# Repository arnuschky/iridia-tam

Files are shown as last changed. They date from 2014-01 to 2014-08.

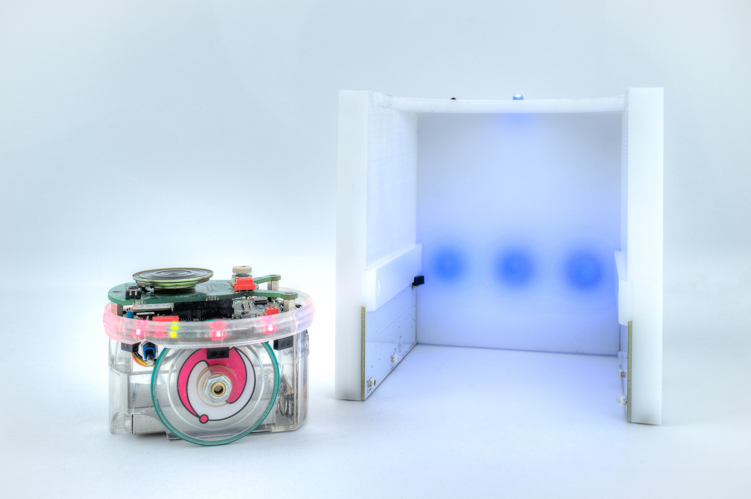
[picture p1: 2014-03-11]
photos/tam_v5_simple_epuck-surreal.jpg

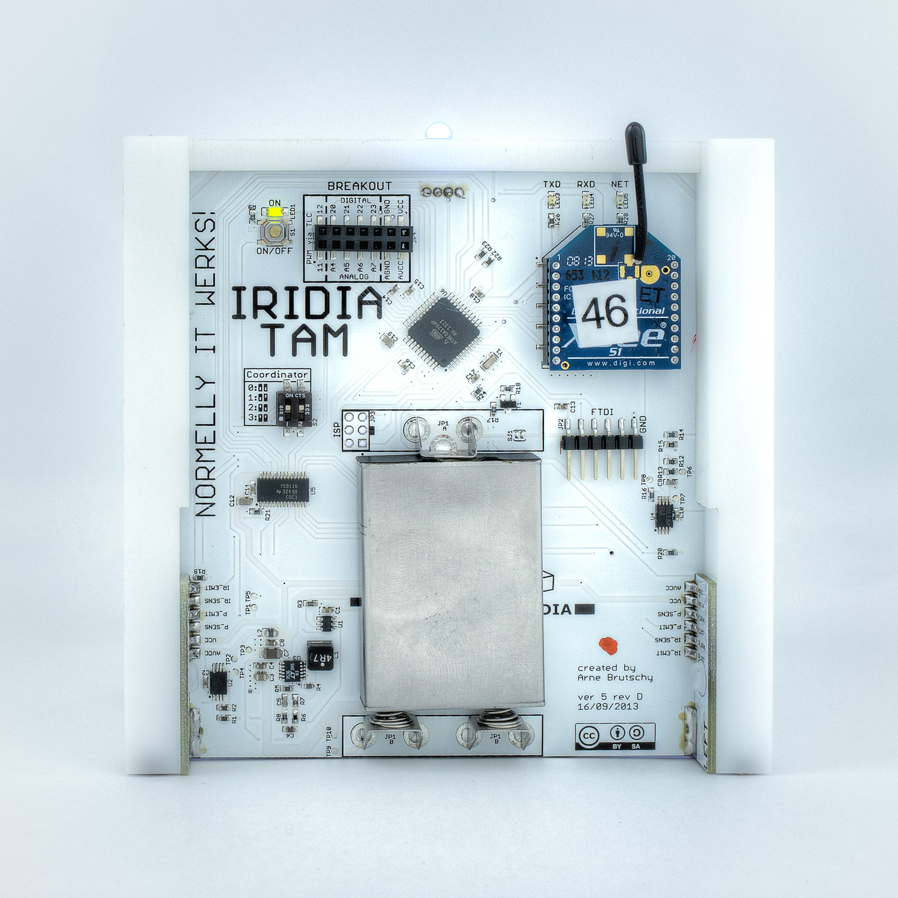
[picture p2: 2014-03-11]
photos/tam_v5_back-surreal.jpg

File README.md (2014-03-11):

IRIDIA-TAM
==========

The IRIDIA TAM (Task Abstraction Module), a device whose function is to represent tasks that have to be performed by e-puck robots in laboratory experiments.

 * Website: http://arnuschky.github.com/iridia-tam/  
 * GitHub: https://github.com/arnuschky/iridia-tam/  
 * Repository: http://arnuschky.github.com/iridia-tam/  
 
Current version of the TAM: version 5, revision D.

The GitHub repository contains all files required for producing and using the TAM. In detail, the different directories contain:

3dmodel
-------

A 3D model of the TAM, created by using the free version of Google Sketchup (version 8). Models of the PCBs have been created using EagleUp (http://eagleup.wordpress.com/).

Additionally, the directory contains 2D plans of the plastic shell in PDF format. These plans were used to produce the plastic shell (machined from POM plastic).

coordinator
----------

This directory contains the coordinator, the central software written in Java that controls all TAMs in a given experiment. The researcher can use the coordinator software to set the behavior of the TAMs, define their interrelationships and collect statistics. Due to the use of Java, the software it platform-independent.

The directory also includes a modified version of the Xbee-api, an open-source project to access Xbee modules using Java. See http://code.google.com/p/xbee-api/ for more information. The project has been adapted to use the Digimesh mesh networking prototcol. If desired, one could also use simple point-to-point communication or the more advanced Zigbee prototcol.

electronics
-----------

This directory contains the project files created using Eagle (non-free version, due to PCB size) and the Arduino libraries and firmware.

### electronics/eagle

Contains the CAD files (board and schematics) for CADSoft Eagle (Version 6). 
Additionally, a library with custom footprints is also included in the repository.

### electronics/arduino

Sourcecode of the TAM's firmware ("sketchbook" in Arduino-speech). There are also a number of libraries included on which the firmware depends. Some of these libraries have been written or modified by us:

 - ircom - library that allows to communicate between the TAM and the epuck using the proximity sensor of the epuck
 - TLC59116 - generic TLC59116 library, adapted from http://brmlab.cz/project/ledbar (CC Attribution-Noncommercial-Share Alike 3.0 Unported License)
 - Xbee - library for using Xbee modules with the Arduino by Andrew Rapp, adapted to work with Digimesh networks and software serial ports (GPL 3)

Others are 3rd party open-source projects included for convenience:

 - I2C - fast I2C library by Wayne Truchsess (LGPL) http://dsscircuits.com/articles/arduino-i2c-master-library.html

photos
------

High-res photos of the TAM version 5, revision D.

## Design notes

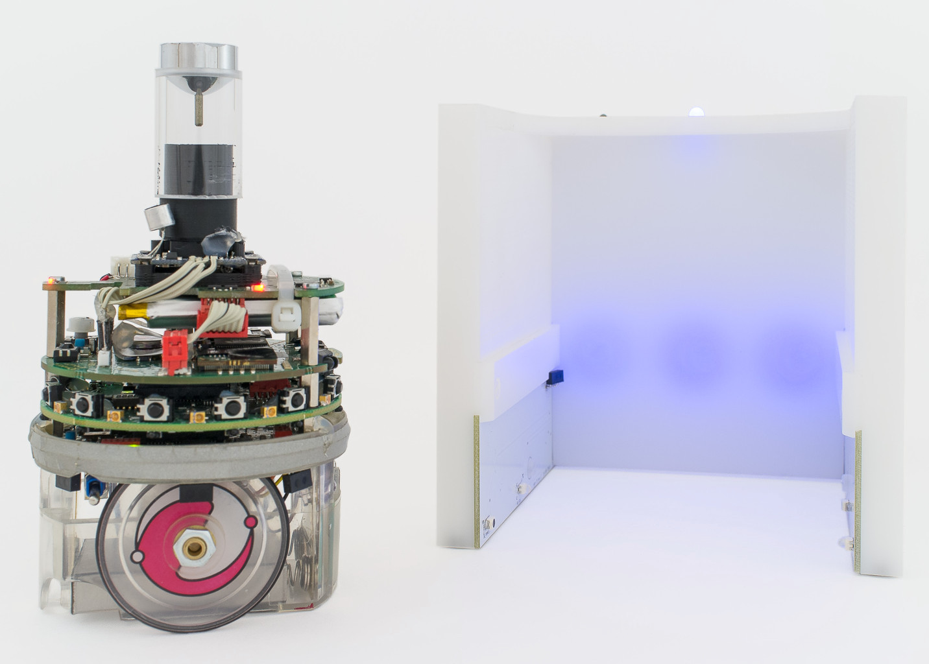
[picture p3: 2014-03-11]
photos/tam_v5_complex_epuck.jpg

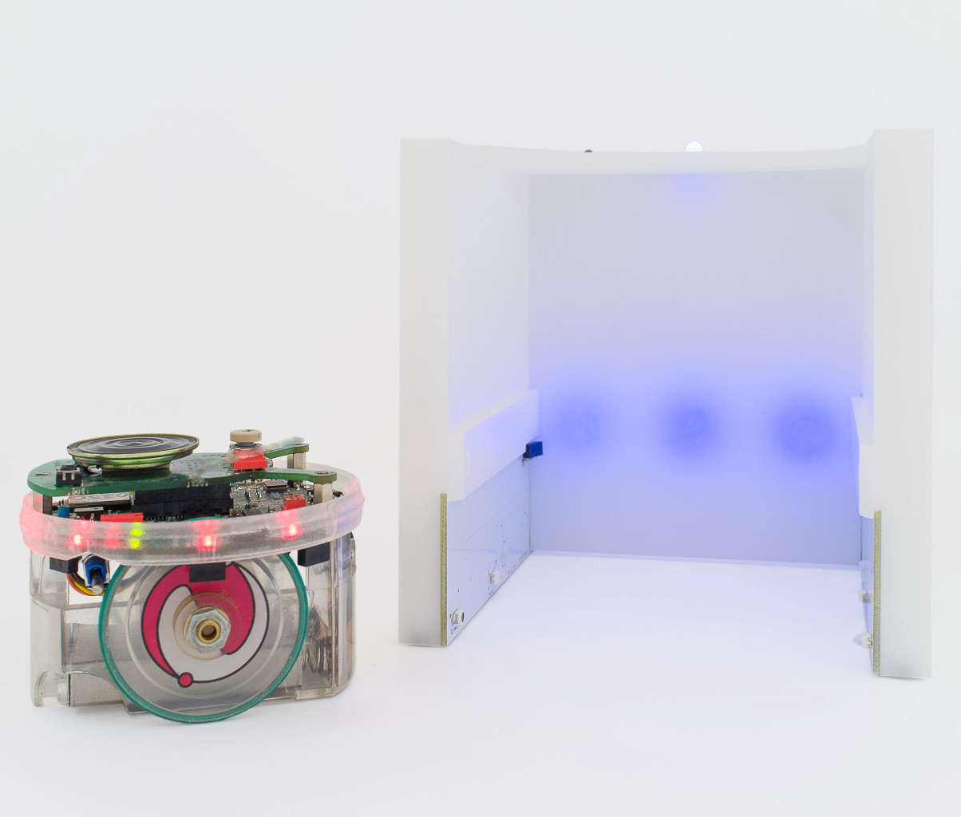
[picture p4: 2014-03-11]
photos/tam_v5_simple_epuck.jpg

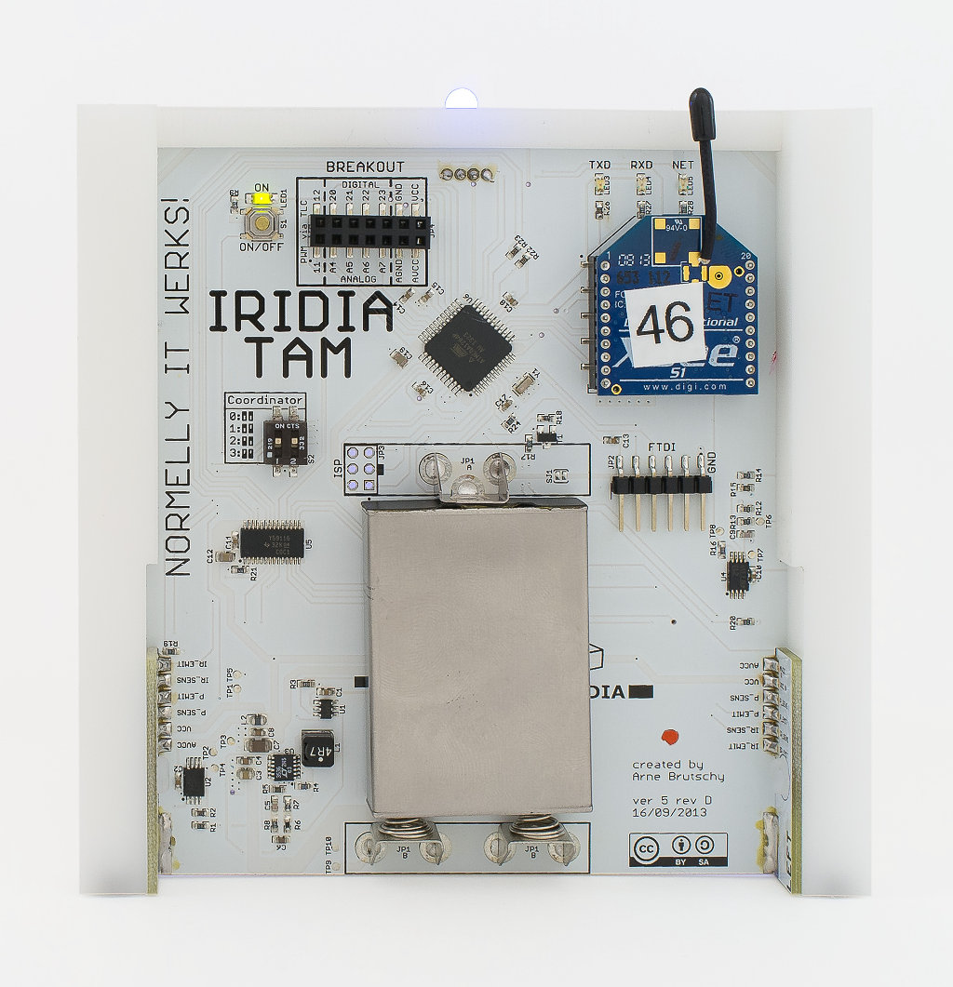
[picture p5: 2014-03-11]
photos/tam_v5_back.jpg

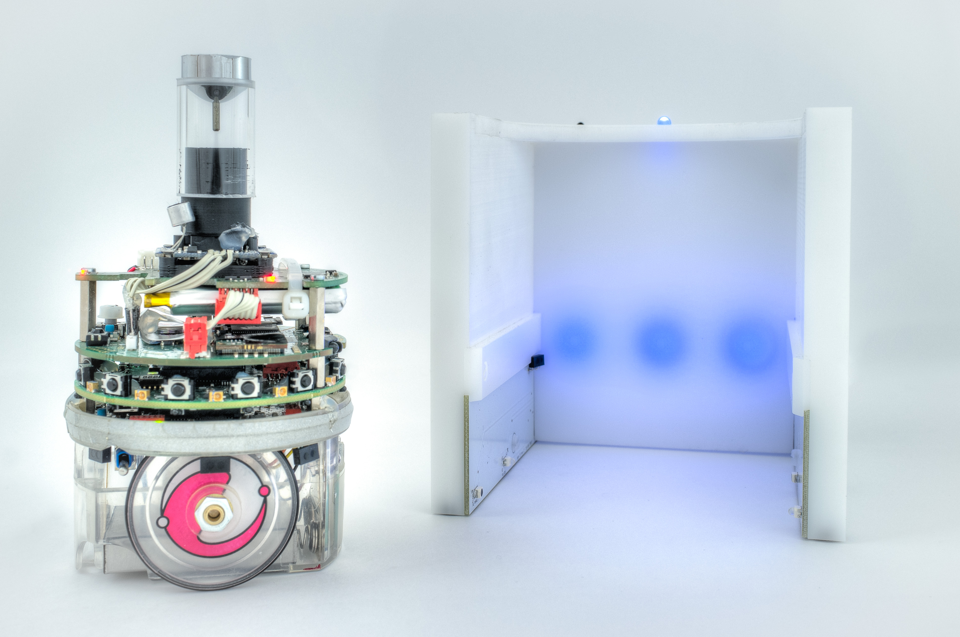
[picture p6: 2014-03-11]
photos/tam_v5_complex_epuck-surreal.jpg

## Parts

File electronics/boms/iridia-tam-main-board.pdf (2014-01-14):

Name | Desc | Package | Manufacturer | Manufacturer part number | Qty | supplier | reference
Y1 | CERAMIC RESONATOR 16.0MHZ SMD | | Murata Electronics | CSTCE16M0V53-R0 | 1 | Digi-Key | 490-1198-1-ND
T1,T2 | TRANSISTOR GP NPN AMP SOT-23 | SOT-23 | Fairchild Semiconductors | MMBT3904FSCT | 2 | Digi-Key | MMBT3904FSCT-ND
U1 | IC CTLR ON/OFF W/DEB TSOT23-6 | 6-SOT23 | Maxim Integrated | MAX16054AZT+T | 1 | Digi-Key | MAX16054AZT+TCT-ND
U2 | IC OPAMP GP 700KHZ DUAL 8TSSOP | 8-TSSOP | Texas Instruments | LM358PWR | 1 | Digi-Key | 296-9555-1-ND
U3 | IC REG BUCK BST SYNC ADJ 12MSOP | 12-MSOP | Linear Technology | LTC3536EMSE#PBF | 1 | Digi-Key | LTC3536EMSE#PBF-ND
U4 | IC VOLT COMPARATOR DUAL 8-TSSOP | 8-TSSOP | STMicroelectronics | LM293PT | 1 | Digi-Key | 497-7818-1-ND
U5 | IC LED DRIVER LINEAR 28-TSSOP | 28-TSSOP | Texas Instruments | TLC59116IPWR | 1 | Digi-Key | 296-23354-1-ND
U6 | IC MCU 8BIT 128KB FLASH 44TQFP | 44-TQFP | Atmel | ATMEGA1284P-AU | 1 | Digi-Key | ATMEGA1284P-AU-ND
U7 | CONN RECEPT 2MM SINGLE SMD 10POS GOLD | 1X10SMD | open/any | NPPN101BFLD-RC | 2 | Digi-Key | S5902-10-ND
JP1A | CONTACT BATT POSITIVE AA/AAA/N | | Keystone Electronics | '637 | 1 | Digi-Key | 637K-ND
JP1B | CONTACT BATT NEG SPRING AA/AAA/N | | Keystone Electronics | '629 | 2 | Digi-Key | 629K-ND
JP2 | CONN HEADER R/A 6POS 90° GOLD SMD | 1X06SMD/90 | open/any | 961106-5500-AR-PR | 1 | Digi-Key | 3M9501CT-ND
JP3 | do not populate
JP4 | CONN FMALE 14POS DL .1" GOLD SMD | 2X07SMD | open/any | NPPC072KFMS-RC | 1 | Digi-Key | S5716-ND
S1 | SWITCH TACTILE SPST-NO 0.05A 12V | | C&K Components | PTS525SM10SMTR LFS | 1 | Digi-Key | CKN9104CT-ND
S2 | SWITCH TAPE SEAL 2 POS SMD | CTS-219-02 | CTS Electrocomponents | 219-2MST | 1 | Digi-Key | CT2192MST-ND
L1 | INDUCTOR POWER 4.7UH 1.3A SMD | VLCF5024T | TDK Corporation | VLCF5024T-4R7N1R3-2 | 1 | Digi-Key | 445-8748-1-ND
L2 | INDUCTOR MULTILAYER 10UH 0805 | '0805 | TDK Corporation | MLZ2012M100W | 1 | Digi-Key | 445-6396-1-ND
LED1 | LED CHIPLED 570NM GREEN 1206 SMD | '1206 | OSRAM Opto Semiconductors | LG N971-KN-1 | 1 | Digi-Key | 475-1407-1-ND
LED2 | do not populate
LED3 | LED YELLOW CLEAR THIN 0805 SMD | '0805 | Lite-On Inc | LTST-C171YKT | 1 | Digi-Key | 160-1431-1-ND
LED4 | LED AMBER CLR THIN 0805 SMD | '0805 | Lite-On Inc | LTST-C171AKT | 1 | Digi-Key | 160-1419-1-ND
LED5 | LED RED ORAN CLEAR THIN 0805 SMD | '0805 | Lite-On Inc | LTST-C171EKT | 1 | Digi-Key | 160-1422-1-ND
RGB_LED_L,RGB_LED_M,RGB_LED_R | LED MULTILED RGB WHT BINNED 6PLC | 6-PLCC | OSRAM Opto Semiconductors | LRTBG6SF-V2BA-3E7F-0-0-ZP | 3 | Digi-Key | 475-2853-1-ND
R1 | RES 42.2k OHM 1/10W 1% 0603 SMD | '0603 | open/any | | 1 | Digi-Key | P42.2KHCT-ND
R2,R22,R23 | RES 4.7k OHM 1/10W 1% 0603 SMD | '0603 | open/any | | 3 | Digi-Key | P4.70KHCT-ND
R3,R8,R16 | RES 1M OHM 1/10W 1% 0603 SMD | '0603 | open/any | | 3 | Digi-Key | P1.00MHCT-ND
R4 | RES 100K OHM 1/10W 1% 0603 SMD | '0603 | open/any | | 1 | Digi-Key | P100KHCT-ND
R5 | RES 49.9k OHM 1/10W 1% 0603 SMD | '0603 | open/any | | 1 | Digi-Key | P49.9KHCT-ND
R6 | RES 6.49k OHM 1/10W 1% 0603 SMD | '0603 | open/any | | 1 | Digi-Key | P6.49KHCT-ND
R7 | RES 221k OHM 1/10W 1% 0603 SMD | '0603 | open/any | | 1 | Digi-Key | P221KHCT-ND
R10,R11 | RES 0.0 OHM 1/10W 5% 0603 SMD | '0603 | open/any | | 2 | Digi-Key | P0.0GCT-ND
R12,R13,R19,R20,R24,R25 | RES 10k OHM 1/10W 5% 0603 SMD | '0603 | open/any | | 6 | Digi-Key | P10KGCT-ND
R14 | RES 47k OHM 1/10W 1% 0603 SMD | '0603 | open/any | | 1 | Digi-Key | P47.0KHCT-ND
R15 | RES 20K OHM 1/10W 1% 0603 SMD | '0603 | open/any | | 1 | Digi-Key | P20.0KHCT-ND
R17 | RES 39 OHM 1/10W 5% 0603 SMD | '0603 | open/any | | 1 | Digi-Key | P39GCT-ND
R18,R21 | RES 470 OHM 1/10W 5% 0603 SMD | '0603 | open/any | | 2 | Digi-Key | P470GCT-ND
R9,R26,R27,R28 | RES 68 OHM 1/10W 5% 0603 SMD | '0603 | open/any | | 4 | Digi-Key | P68GCT-ND
C1,C2,C10,C11,C13,C14,C15,C16,C17,C18 | CAP CER 0.1UF 16V 10% X7R 0603 | '0603 | Taiyo Yuden | EMK107B7104KA-T | 10 | Digi-Key | 587-1240-1-ND
C3,C12,C19 | CAP CER 10UF 10V 10% X5R 0805 | '0805 | Murata Electronics | GRM21BR61A106KE19L | 3 | Digi-Key | 490-1709-1-ND
C4,C8 | CAP CER 1UF 16V 10% X7R 0603 | '0603 | TDK Corporation | C1608X7R1C105K080AC | 2 | Digi-Key | 445-1604-1-ND
C5 | CAP CER 220PF 50V 5% NP0 0603 | '0603 | TDK Corporation | C1608C0G1H221J080AA | 1 | Digi-Key | 445-1285-1-ND
C6 | CAP CER 47PF 50V 5% NP0 0603 | '0603 | TDK Corporation | C1608C0G1H470J080AA | 1 | Digi-Key | 445-1277-1-ND
C7 | CAP CER 22UF 6.3V 10% X5R 1206 | '1206 | AVX Corporation | 12066D226KAT2A | 1 | Digi-Key | 478-1576-1-ND
C9 | CAP CER 100PF 16V 10% X7R 0603 | '0603 | open/any | | 1 | Digi-Key | 478-6207-1-ND

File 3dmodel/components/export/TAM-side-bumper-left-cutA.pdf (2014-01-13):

## Cut A view

TAM-side-bumper-left

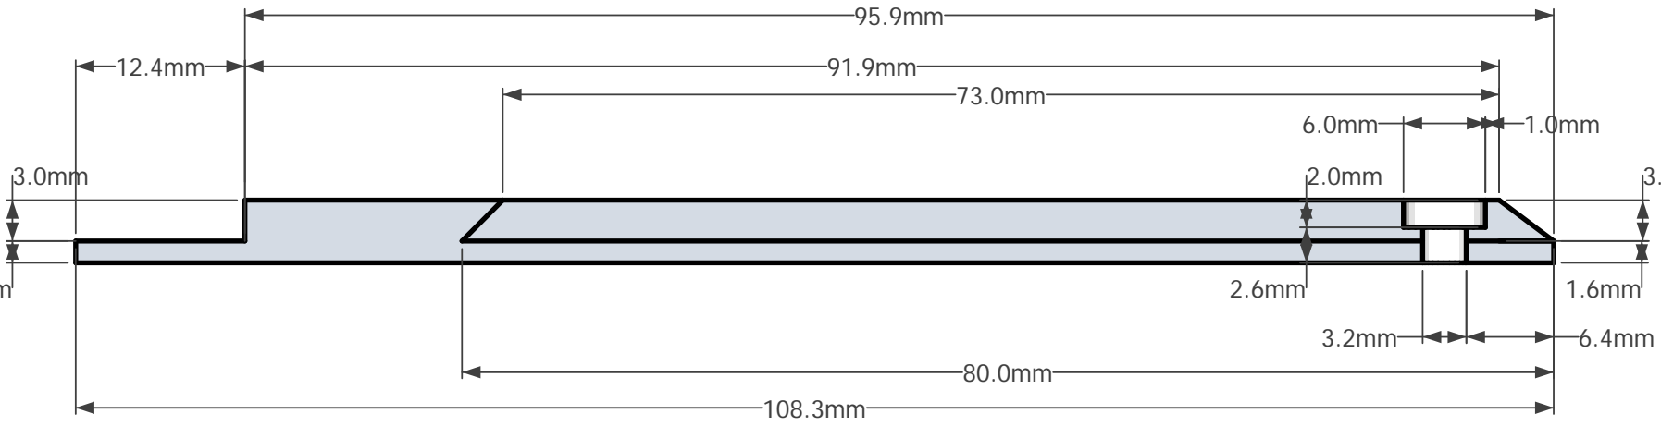
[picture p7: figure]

1.6mm

3.0mm

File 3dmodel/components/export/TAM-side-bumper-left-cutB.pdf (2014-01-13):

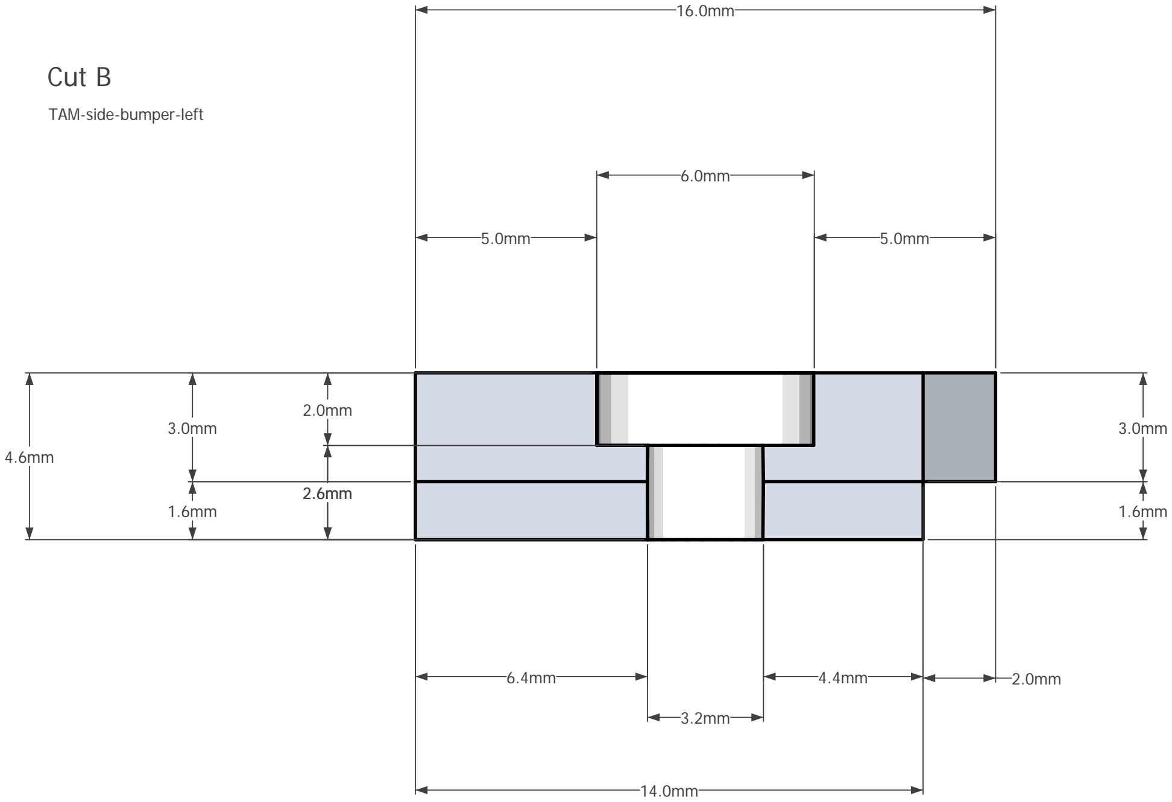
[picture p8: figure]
Cut B; TAM-side-bumper-left

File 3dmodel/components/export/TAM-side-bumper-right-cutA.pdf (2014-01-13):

TAM-side-bumper-right

## Cut A

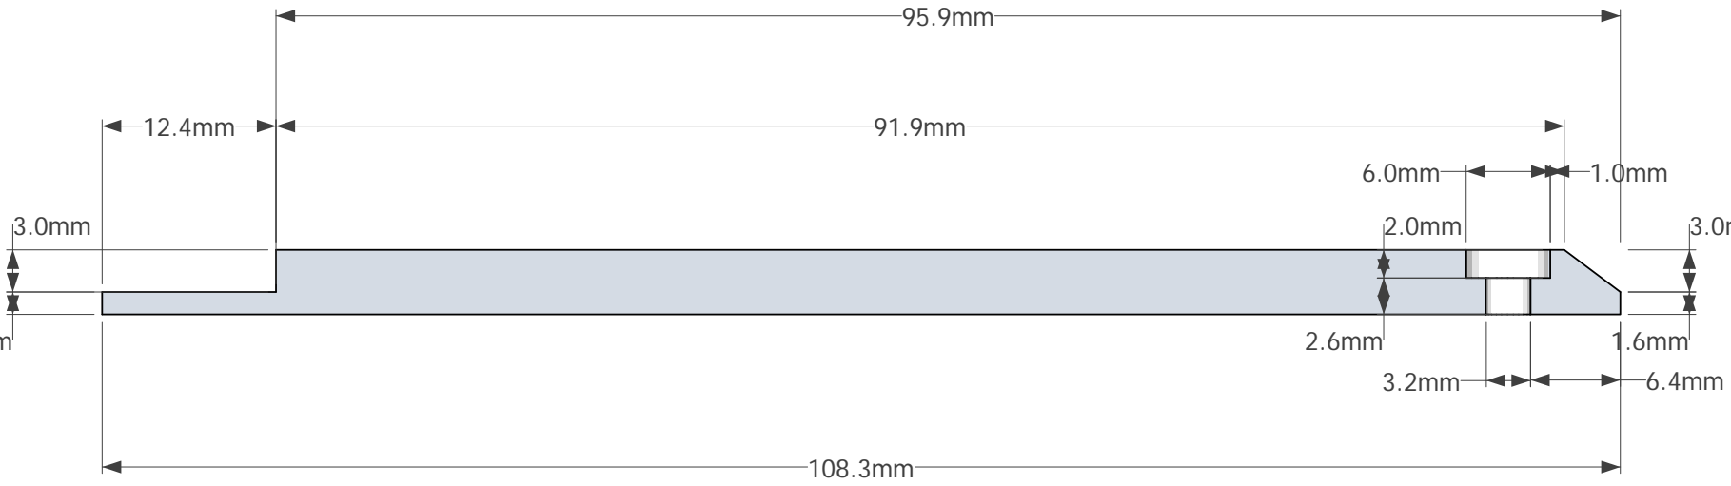
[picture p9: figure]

1.6mm

3.0mm

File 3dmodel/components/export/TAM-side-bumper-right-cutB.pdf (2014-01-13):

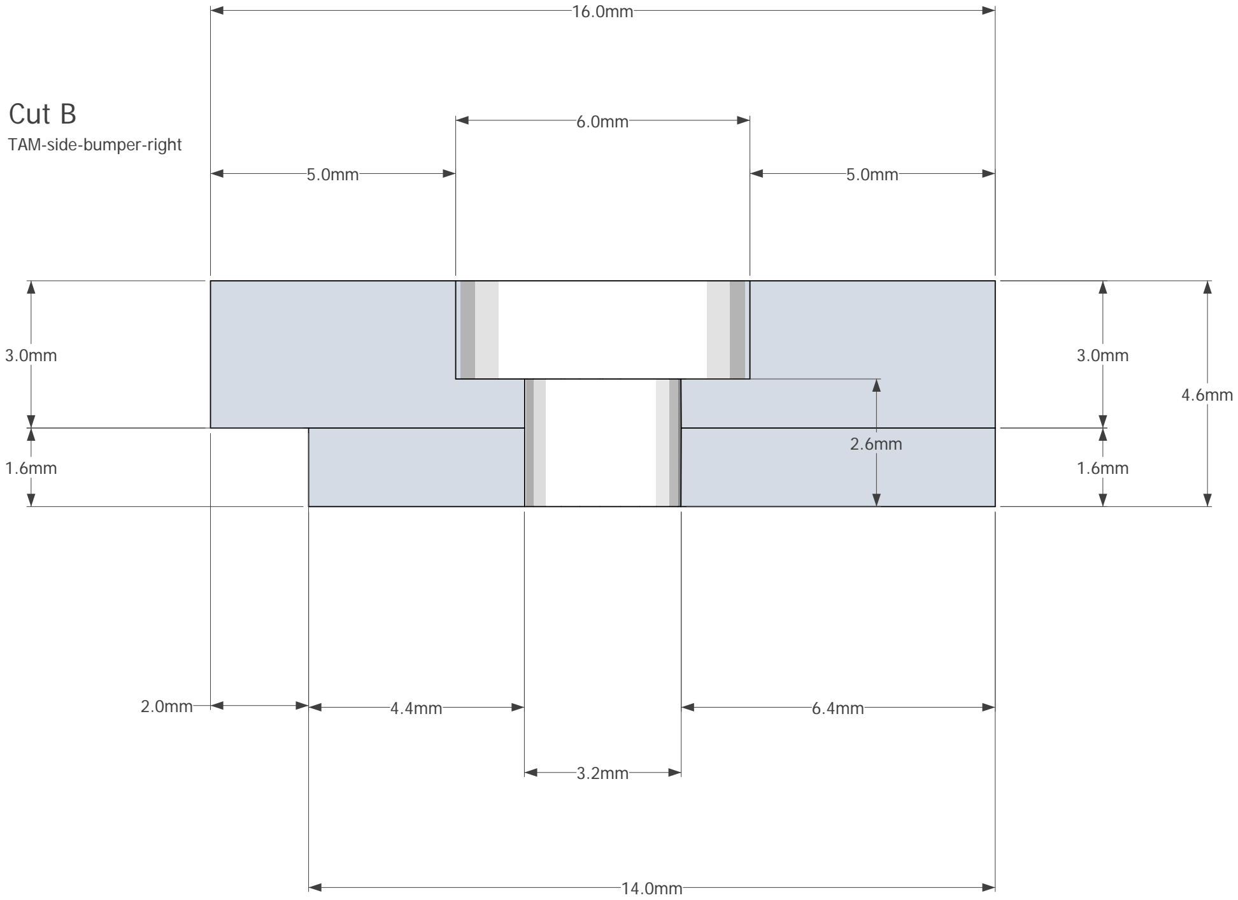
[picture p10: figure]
Cut B; TAM-side-bumper-right

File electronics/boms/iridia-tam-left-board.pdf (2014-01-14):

Name | Desc | Value | Package | Manufacturer | Manufacturer part number | Qty | Example supplier | Example supplier reference
IR_LED_L | IR EMITTER | SFH 4258 | 4-PLCC | OSRAM Opto SemiconductorsSFH4258-Z | | 1 | Digi-Key | 475-1243-1-ND
IR_TRANSISTOR_L | IR PHOTOTRANSISTOR | SFH 320 FA-Z | PLCC-2 | OSRAM Opto SemiconductorsSFH320FA-Z | | 1 | Mouser | 720-SFH320FA-Z
PROX_L | do not populate

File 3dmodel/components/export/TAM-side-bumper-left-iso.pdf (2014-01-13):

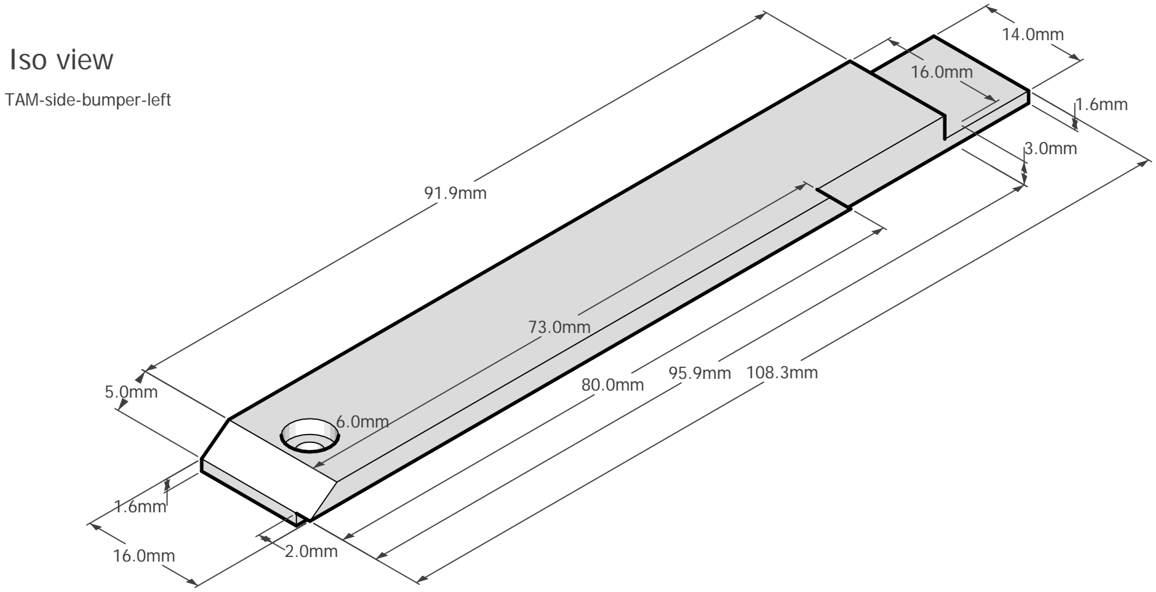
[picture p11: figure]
Iso view; TAM-side-bumper-left

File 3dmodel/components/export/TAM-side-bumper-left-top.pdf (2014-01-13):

## Top view

TAM-side-bumper-left

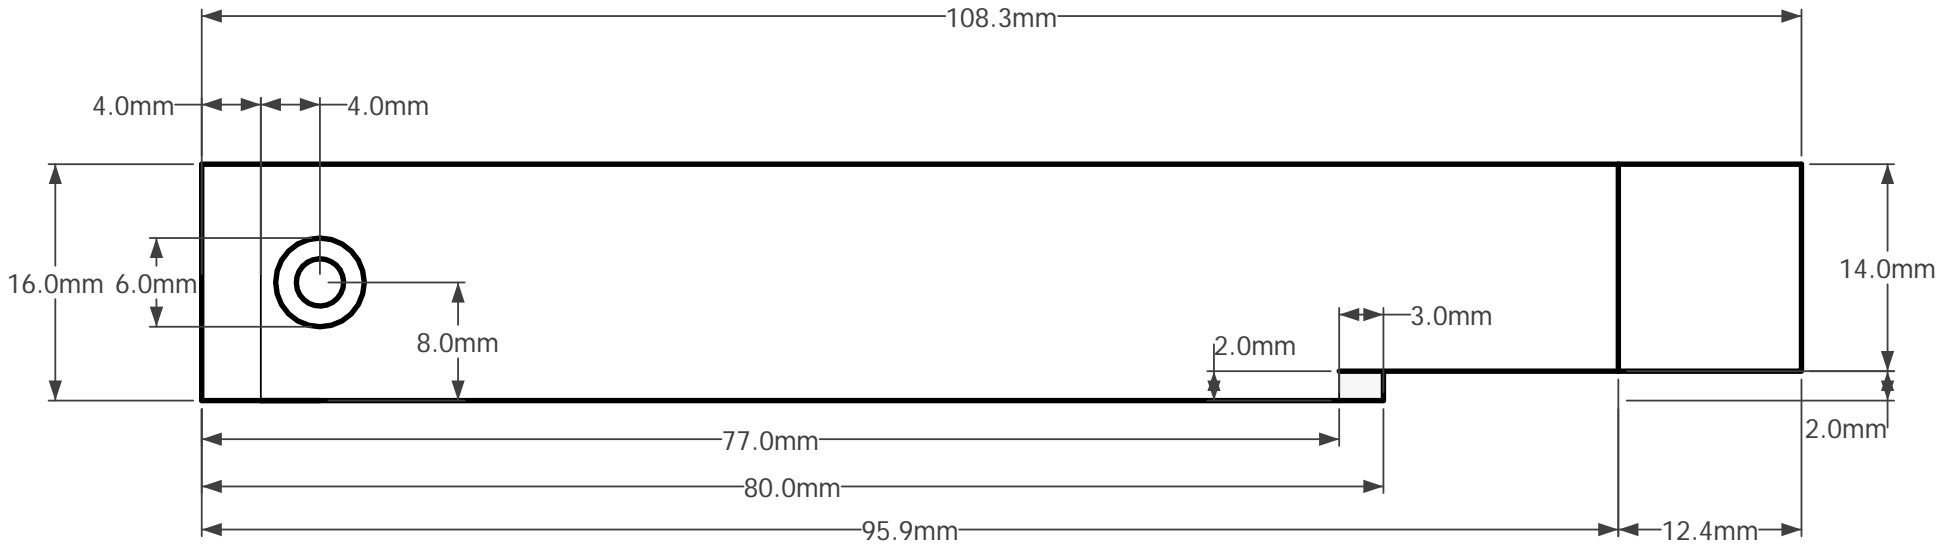
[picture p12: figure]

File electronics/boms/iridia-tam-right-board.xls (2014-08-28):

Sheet: TAM ver5 revC LEFT
Name | Desc | Value | Package | Manufacturer | Manufacturer part number | Qty | Example supplier | Example supplier reference
IR_LED_L | IR EMITTER | SFH 4258 | 4-PLCC | OSRAM Opto Semiconductors | SFH4258-Z | 1 | Digi-Key | 475-1243-1-ND
IR_TRANSISTOR_L | IR PHOTOTRANSISTOR | SFH 320 FA-Z | PLCC-2 | OSRAM Opto Semiconductors | SFH320FA-Z | 1 | Mouser | 720-SFH320FA-Z
PROX_L | do not populate

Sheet: TAM ver5 revC RIGHT
Name | Desc | Value | Package | Manufacturer | Manufacturer part number | Qty | Example supplier | Example supplier reference
IR_LED_R | IR EMITTER | SFH 4258 | 4-PLCC | OSRAM Opto Semiconductors | SFH4258-Z | 1 | Digi-Key | 475-1243-1-ND
IR_TRANSISTOR_R | IR PHOTOTRANSISTOR | SFH 320 FA-Z | PLCC-2 | OSRAM Opto Semiconductors | SFH320FA-Z | 1 | Mouser | 720-SFH320FA-Z

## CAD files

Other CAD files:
3dmodel/TAM-assembly-ver5-revA.skp
3dmodel/components/TAM-diffuser.skp
3dmodel/components/TAM-side-bumper-left.skp
3dmodel/components/TAM-side-bumper-right.skp
3dmodel/components/TAM-side-shell-left.skp
3dmodel/components/TAM-side-shell-right.skp
3dmodel/components/TAM-top-shell.skp

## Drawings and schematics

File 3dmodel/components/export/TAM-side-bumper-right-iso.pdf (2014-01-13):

## Iso view

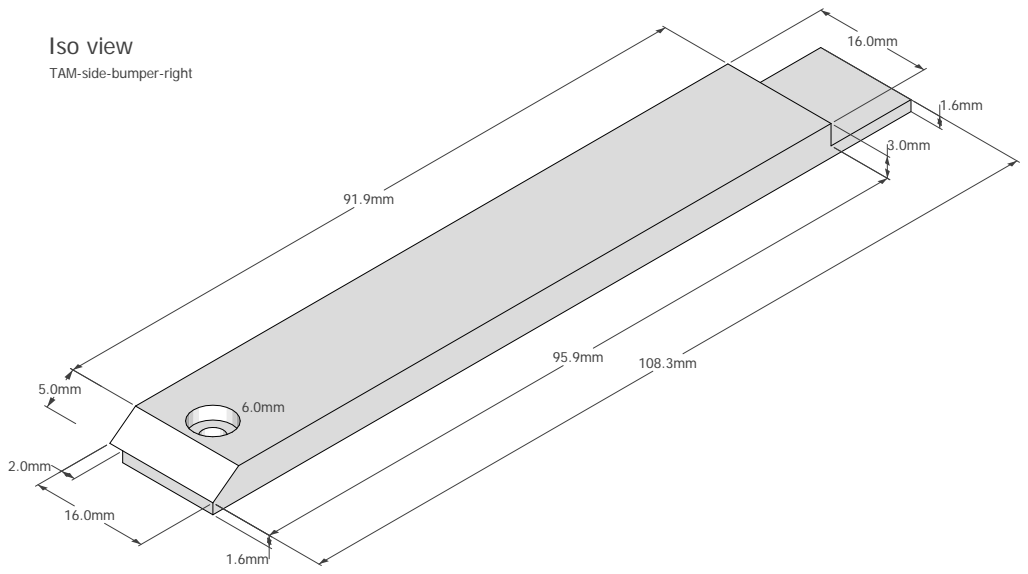
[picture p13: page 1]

TAM-side-bumper-right

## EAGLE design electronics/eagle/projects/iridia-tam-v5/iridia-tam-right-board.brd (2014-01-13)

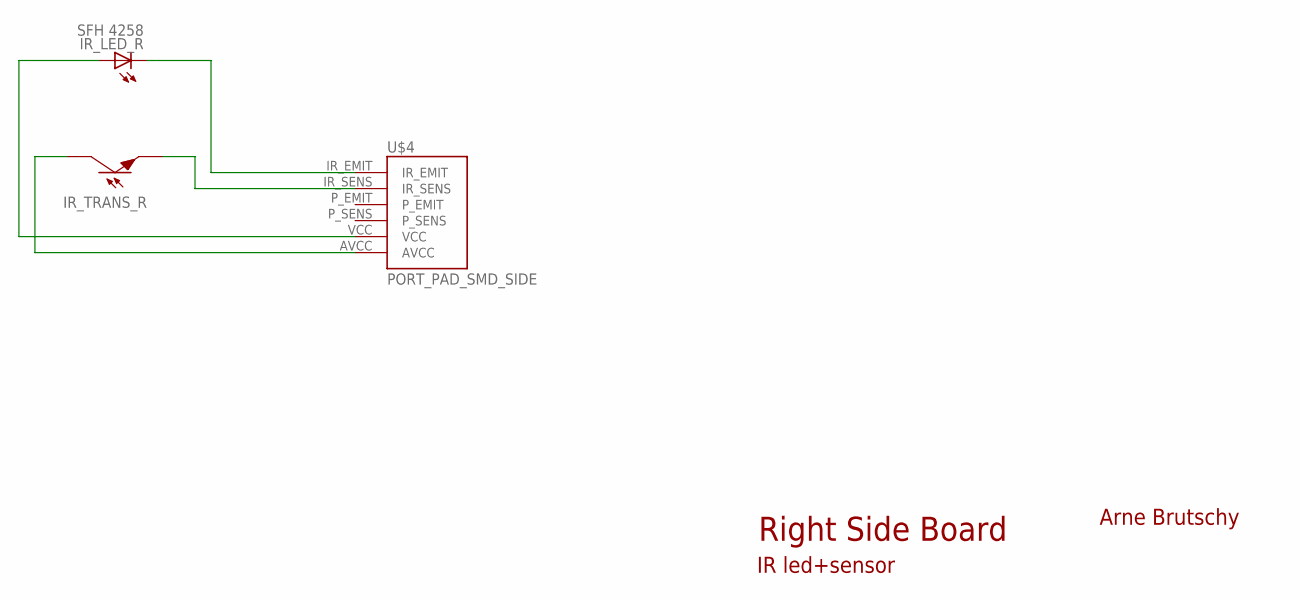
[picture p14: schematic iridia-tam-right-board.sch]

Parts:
IR_LED_R: SFH 4258; P-LCC-4-1C-3A
IR_TRANS_R: SFH 320 FA; P-LCC-2-TRANS
U$4: PORT_PAD_SMD_SIDE

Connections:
IR_EMIT_R: IR_LED_R.C@1 (C), U$4.IR_EMIT
IR_SENSE_R: IR_TRANS_R.E, U$4.IR_SENS
unnamed: IR_TRANS_R.COL, U$4.AVCC
VCC: IR_LED_R.A@2 (A), IR_LED_R.A@3 (A), IR_LED_R.A@4 (A), U$4.VCC

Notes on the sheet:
Right Side Board
IR led+sensor
Arne Brutschy

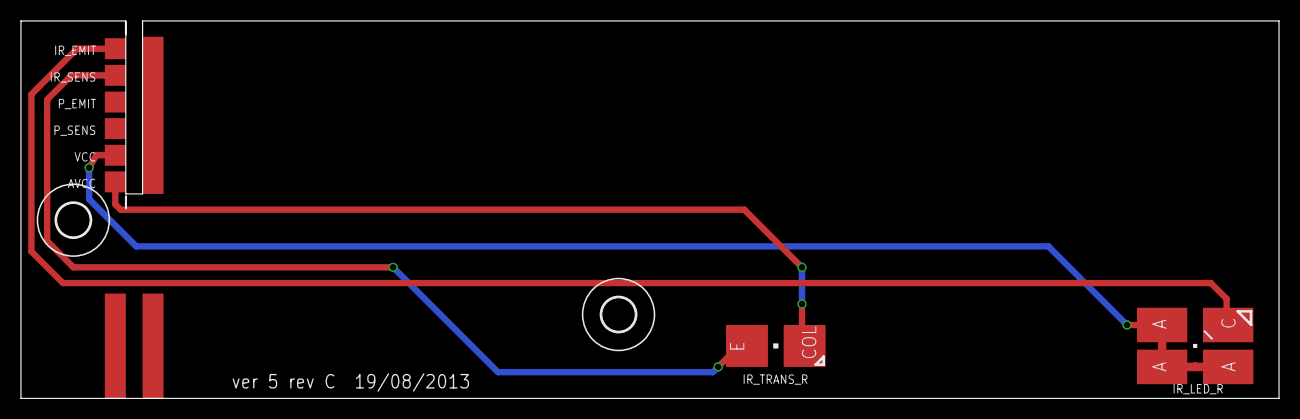
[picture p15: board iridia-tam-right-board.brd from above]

Board: 2 copper layers, 120.0 x 36.0 mm, 5 parts (0 on the bottom side), 4 nets.

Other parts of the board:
U$1, U$3: 3,2

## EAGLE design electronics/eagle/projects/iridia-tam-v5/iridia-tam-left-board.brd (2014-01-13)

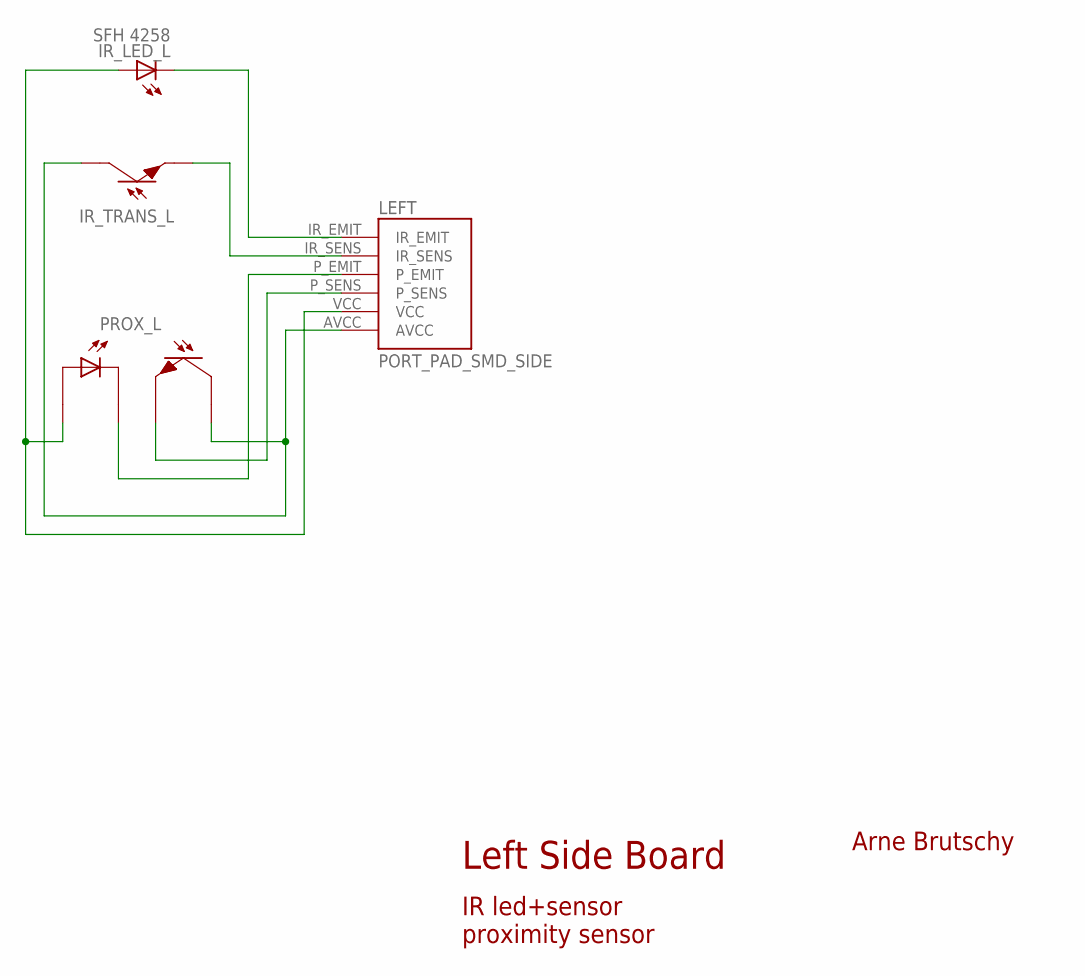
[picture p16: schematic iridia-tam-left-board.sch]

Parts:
IR_LED_L: SFH 4258; P-LCC-4-1C-3A
IR_TRANS_L: SFH 320 FA; P-LCC-2-TRANS
LEFT: PORT_PAD_SMD_SIDE
PROX_L: TCRT1000; TCRT1000_TH

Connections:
AVCC: IR_TRANS_L.COL, LEFT.AVCC, PROX_L.COL
IR_EMIT_L: IR_LED_L.C@1 (C), LEFT.IR_EMIT
IR_SENSE_L: IR_TRANS_L.E, LEFT.IR_SENS
PROX_EMIT: LEFT.P_EMIT, PROX_L.CAT
PROX_SENSE: LEFT.P_SENS, PROX_L.E
VCC: IR_LED_L.A@2 (A), IR_LED_L.A@3 (A), IR_LED_L.A@4 (A), LEFT.VCC, PROX_L.A

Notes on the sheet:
Left Side Board
IR led+sensor proximity sensor
Arne Brutschy

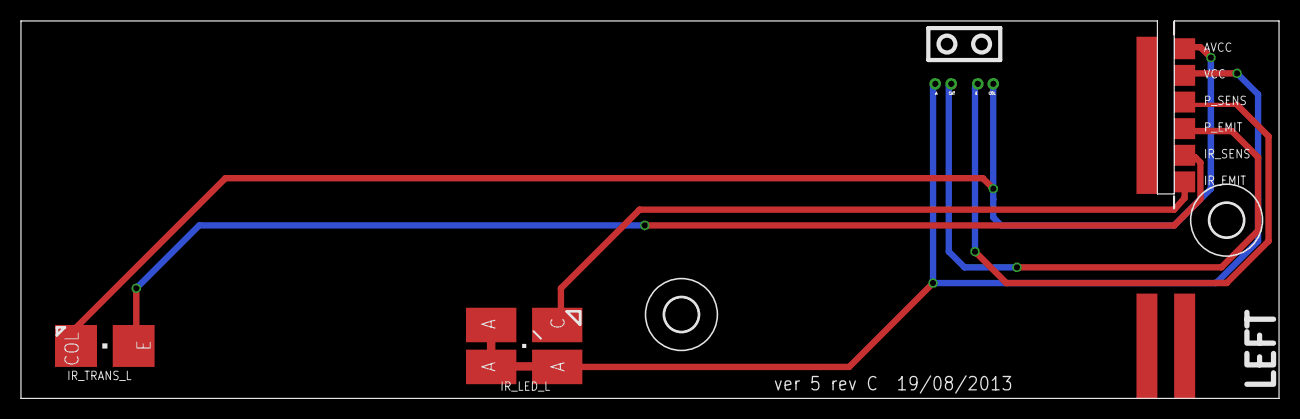
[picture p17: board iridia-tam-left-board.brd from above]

Board: 2 copper layers, 120.0 x 36.0 mm, 6 parts (0 on the bottom side), 6 nets.

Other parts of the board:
U$2, U$3: 3,2

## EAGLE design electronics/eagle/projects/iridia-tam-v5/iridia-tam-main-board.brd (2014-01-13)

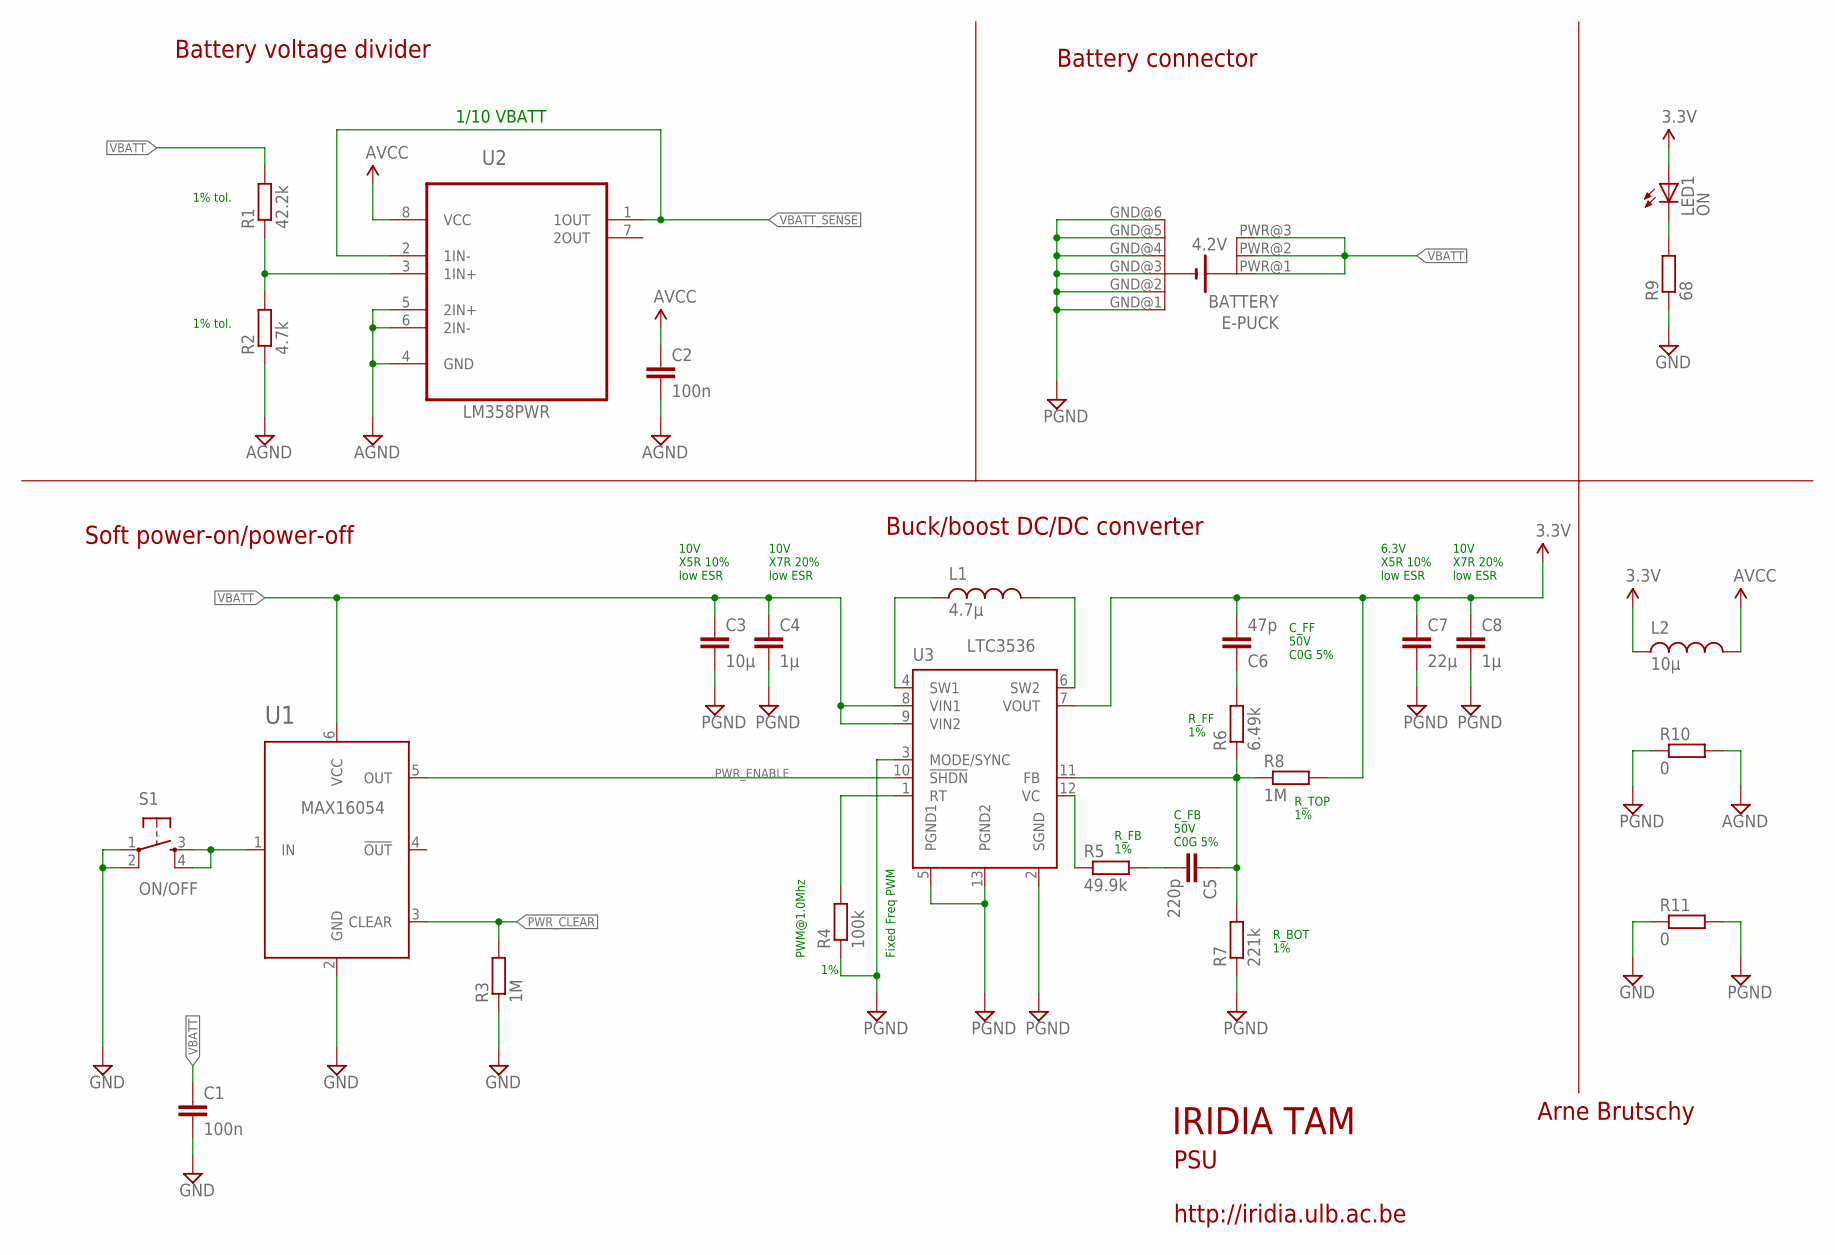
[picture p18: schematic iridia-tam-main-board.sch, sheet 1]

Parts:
C1, C2: 100n; C0603
C3: 10µ; C0805
C4, C8: 1µ; C0603
C5: 220p; C0603
C6: 47p; C0603
C7: 22µ; C1206
JP1: EPUCK_BATTERY
L1: 4.7µ; TDK-VLCF
L2: 10µ; L0805
LED1: ON; CHIPLED_1206
R1: 42.2k; R0603
R2: 4.7k; R0603
R3, R8: 1M; R0603
R4: 100k; R0603
R5: 49.9k; R0603
R6: 6.49k; R0603
R7: 221k; R0603
R9: 68; R0603
R10, R11: 0; R0603
S1: ON/OFF; TACTILE_SWITCH_SMD
U1: MAX16054; SOT23-6-INV
U2: LM358PW; SOP65P640X120-8N
U3: LTC3536; MSOP12-EP

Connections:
AGND: C2.2, R2.1, R10.2, U2.4 (GND), U2.5 (2IN+), U2.6 (2IN-); also elsewhere on the board
AVCC: C2.1, L2.2, U2.8 (VCC); also elsewhere on the board
GND: C1.2, R3.1, R9.1, R11.1, S1.1, S1.2, U1.2 (GND); also elsewhere on the board
unnamed: C6.1, R6.2
unnamed: R4.2, U3.1 (RT)
unnamed: R1.1, R2.2, U2.3 (1IN+)
unnamed: LED1.C, R9.2
unnamed: L1.P$1, U3.4 (SW1)
unnamed: L1.P$2, U3.6 (SW2)
unnamed: S1.3, S1.4, U1.1 (IN)
unnamed: R5.1, U3.12 (VC)
unnamed: C5.1, R6.1, R7.2, R8.1, U3.11 (FB)
unnamed: C5.2, R5.2
PGND: C3.2, C4.2, C7.2, C8.2, JP1.GND@1 (-1), JP1.GND@2 (-2), JP1.GND@3 (-3), JP1.GND@4 (-4), JP1.GND@5 (-5), JP1.GND@6 (-6), R4.1, R7.1, R10.1, R11.2, U3.2 (SGND), U3.3 (MODE/SYNC), U3.5 (PGND1), U3.13 (PGND2); also elsewhere on the board
PWR_CLEAR: R3.2, U1.3 (CLEAR); also elsewhere on the board
PWR_ENABLE: U1.5 (OUT), U3.10 (!SHDN)
VBATT: C1.1, C3.1, C4.1, JP1.PWR@1 (+1), JP1.PWR@2 (+2), JP1.PWR@3 (+3), R1.2, U1.6 (VCC), U3.8 (VIN1), U3.9 (VIN2); also elsewhere on the board
VBATT_SENSE: U2.1 (1OUT), U2.2 (1IN-); also elsewhere on the board
VCC: C6.2, C7.1, C8.1, L2.1, LED1.A, R8.2, U3.7 (VOUT); also elsewhere on the board

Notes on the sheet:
IRIDIA TAM
Arne Brutschy
http://iridia.ulb.ac.be
PSU
PWM@1.0Mhz
R_FF 1%
C_FF 50V C0G 5%
R_TOP 1%
R_FB 1%
C_FB 50V C0G 5%
R_BOT 1%
1/10 VBATT
Battery voltage divider
LM358PWR
Battery connector
Buck/boost DC/DC converter
Soft power-on/power-off
LTC3536
1% tol.
6.3V X5R 10% low ESR
Fixed Freq PWM
10V X7R 20% low ESR
10V X5R 10% low ESR

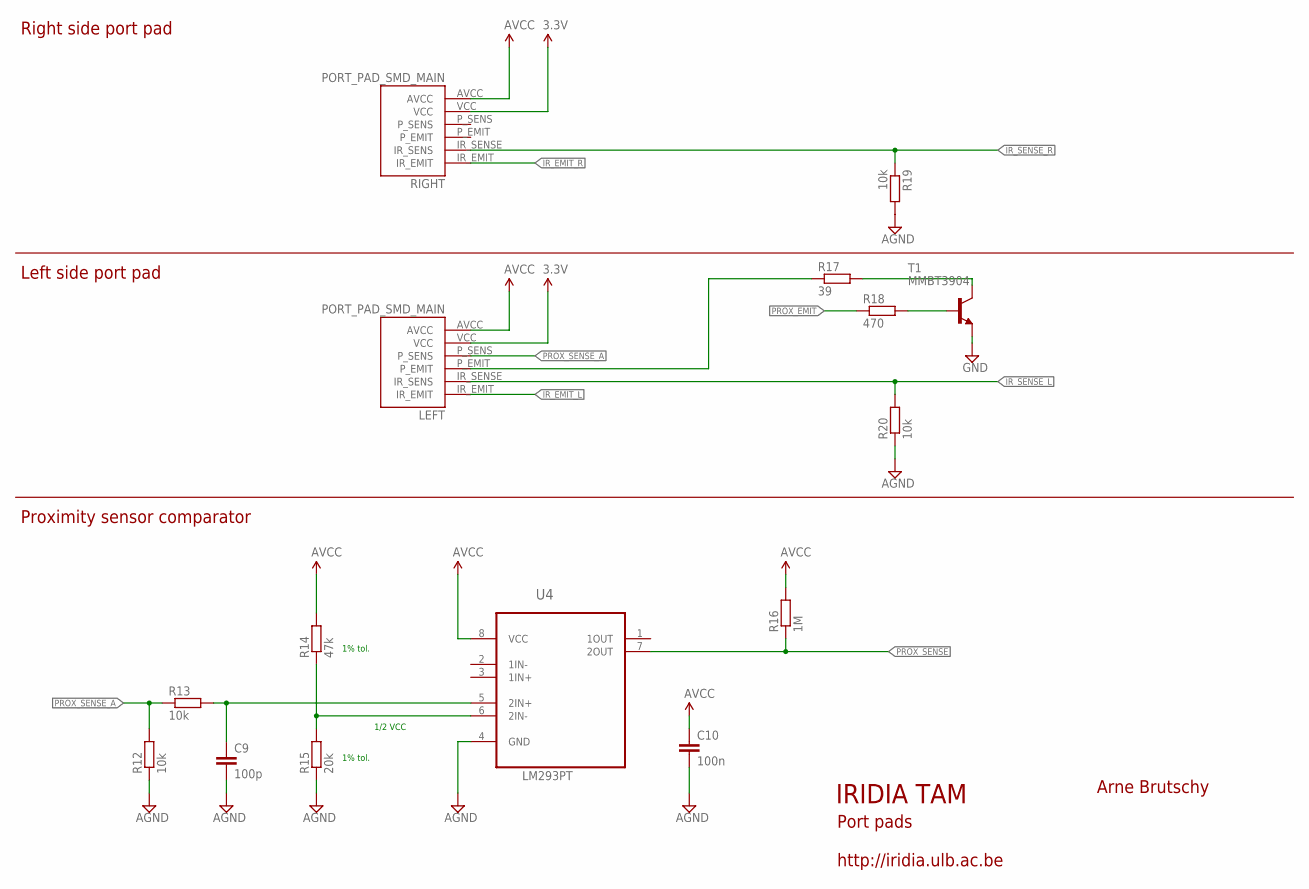
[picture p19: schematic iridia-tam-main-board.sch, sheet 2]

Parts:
C9: 100p; C0603
C10: 100n; C0603
LEFT: PORT_PAD_SMD_MAIN
R12, R13, R19, R20: 10k; R0603
R14: 47k; R0603
R15: 20k; R0603
R16: 1M; R0603
R17: 39; R0603
R18: 470; R0603
RIGHT: PORT_PAD_SMD_MAIN
T1: MMBT3904; SOT23-BEC
U4: LM293PT; 8-TSSOP_4.4MM

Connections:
AGND: C9.2, C10.2, R12.1, R15.1, R19.2, R20.1, U4.4 (GND); also elsewhere on the board
AVCC: C10.1, LEFT.AVCC, R14.2, R16.2, RIGHT.AVCC, U4.8 (VCC); also elsewhere on the board
GND: T1.E; also elsewhere on the board
IR_EMIT_L: LEFT.IR_EMIT; also elsewhere on the board
IR_EMIT_R: RIGHT.IR_EMIT; also elsewhere on the board
IR_SENSE_L: LEFT.IR_SENSE (IR_SENS), R20.2; also elsewhere on the board
IR_SENSE_R: R19.1, RIGHT.IR_SENSE (IR_SENS); also elsewhere on the board
unnamed: LEFT.P_EMIT, R17.1
unnamed: R14.1, R15.2, U4.6 (2IN-)
unnamed: R18.2, T1.B
unnamed: R17.2, T1.C
PROX_EMIT: R18.1; also elsewhere on the board
PROX_SENSE: R16.1, U4.7 (2OUT); also elsewhere on the board
PROX_SENSE_A: LEFT.P_SENS, R12.2, R13.1; also elsewhere on the board
PROX_SENSE_S: C9.1, R13.2, U4.5 (2IN+); also elsewhere on the board
VCC: LEFT.VCC, RIGHT.VCC; also elsewhere on the board

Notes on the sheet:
IRIDIA TAM
Arne Brutschy
http://iridia.ulb.ac.be
Port pads
1/2 VCC
Proximity sensor comparator
LM293PT
Left side port pad
Right side port pad
1% tol.

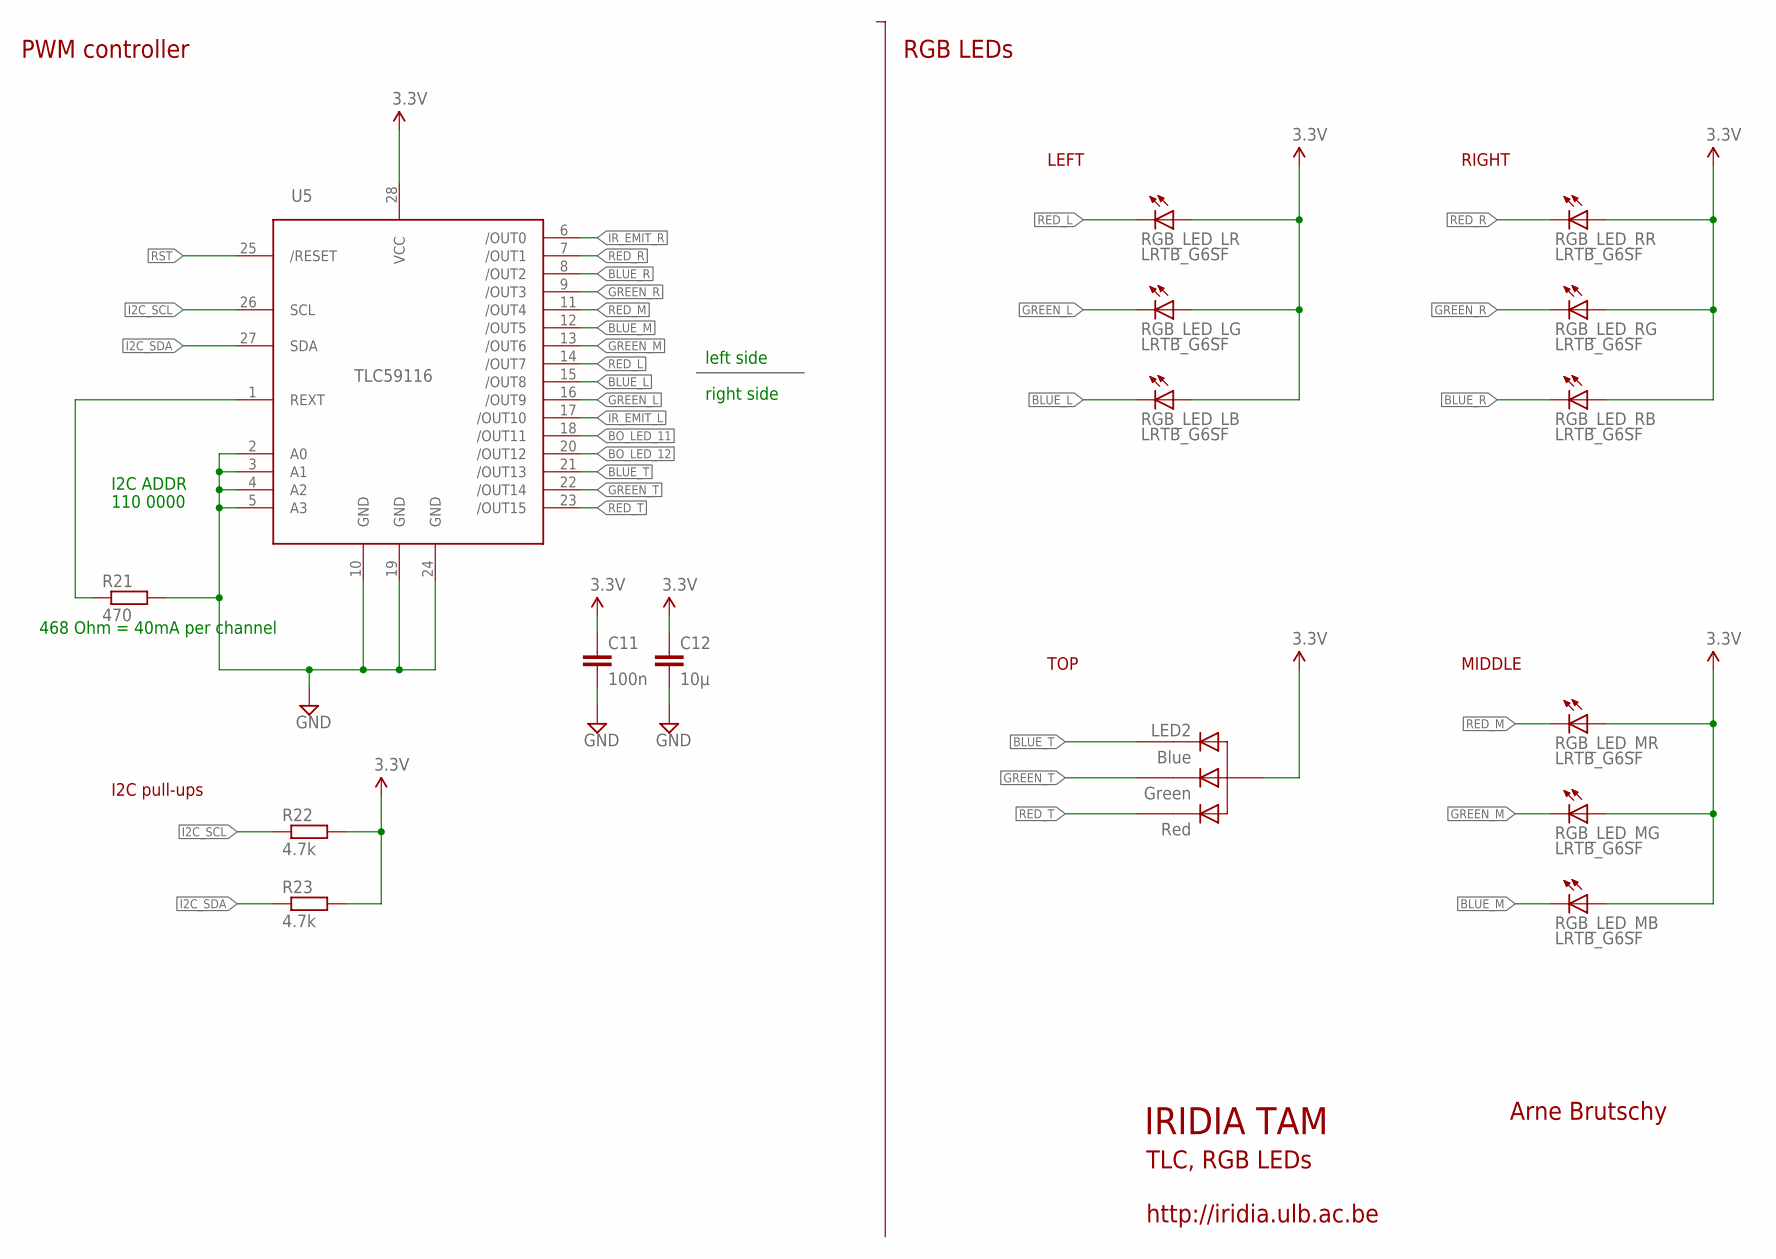
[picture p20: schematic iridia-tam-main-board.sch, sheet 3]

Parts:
C11: 100n; C0603
C12: 10µ; C0805
LED2: RGBLED_CA5MMTROUGHHOLE; LED5MMRGB
R21: 470; R0603
R22, R23: 4.7k; R0603
RGB_LED_L: LRTB_G6SF; P-LCC-6_TOPLED
RGB_LED_M: LRTB_G6SF; P-LCC-6_TOPLED
RGB_LED_R: LRTB_G6SF; P-LCC-6_TOPLED
U5: TLC59116-TSSOP; TSSOP28

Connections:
BLUE_L: RGB_LED_L.C3 (C), U5.15 (/OUT8)
BLUE_M: RGB_LED_M.C3 (C), U5.12 (/OUT5)
BLUE_R: RGB_LED_R.C3 (C), U5.8 (/OUT2)
BLUE_T: LED2.4 (CB), U5.21 (/OUT13)
BO_LED_11: U5.18 (/OUT11); also elsewhere on the board
BO_LED_12: U5.20 (/OUT12); also elsewhere on the board
GND: C11.2, C12.2, R21.2, U5.2 (A0), U5.3 (A1), U5.4 (A2), U5.5 (A3), U5.10 (GND), U5.19 (GND), U5.24 (GND); also elsewhere on the board
GREEN_L: RGB_LED_L.C2 (C), U5.16 (/OUT9)
GREEN_M: RGB_LED_M.C2 (C), U5.13 (/OUT6)
GREEN_R: RGB_LED_R.C2 (C), U5.9 (/OUT3)
GREEN_T: LED2.3 (CG), U5.22 (/OUT14)
I2C_SCL: R22.1, U5.26 (SCL); also elsewhere on the board
I2C_SDA: R23.1, U5.27 (SDA); also elsewhere on the board
IR_EMIT_L: U5.17 (/OUT10); also elsewhere on the board
IR_EMIT_R: U5.6 (/OUT0); also elsewhere on the board
RED_L: RGB_LED_L.C1 (C), U5.14 (/OUT7)
RED_M: RGB_LED_M.C1 (C), U5.11 (/OUT4)
RED_R: RGB_LED_R.C1 (C), U5.7 (/OUT1)
RED_T: LED2.1 (CR), U5.23 (/OUT15)
REXT: R21.1, U5.1 (REXT)
RST: U5.25 (/RESET); also elsewhere on the board
VCC: C11.1, C12.1, LED2.2 (A), R22.2, R23.2, RGB_LED_L.A1 (A), RGB_LED_L.A2 (A), RGB_LED_L.A3 (A), RGB_LED_M.A1 (A), RGB_LED_M.A2 (A), RGB_LED_M.A3 (A), RGB_LED_R.A1 (A), RGB_LED_R.A2 (A), RGB_LED_R.A3 (A), U5.28 (VCC); also elsewhere on the board

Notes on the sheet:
IRIDIA TAM
Arne Brutschy
http://iridia.ulb.ac.be
TLC, RGB LEDs
LEFT
RIGHT
MIDDLE
TOP
I2C ADDR
110 0000
468 Ohm = 40mA per channel
I2C pull-ups
PWM controller
RGB LEDs
left side
right side

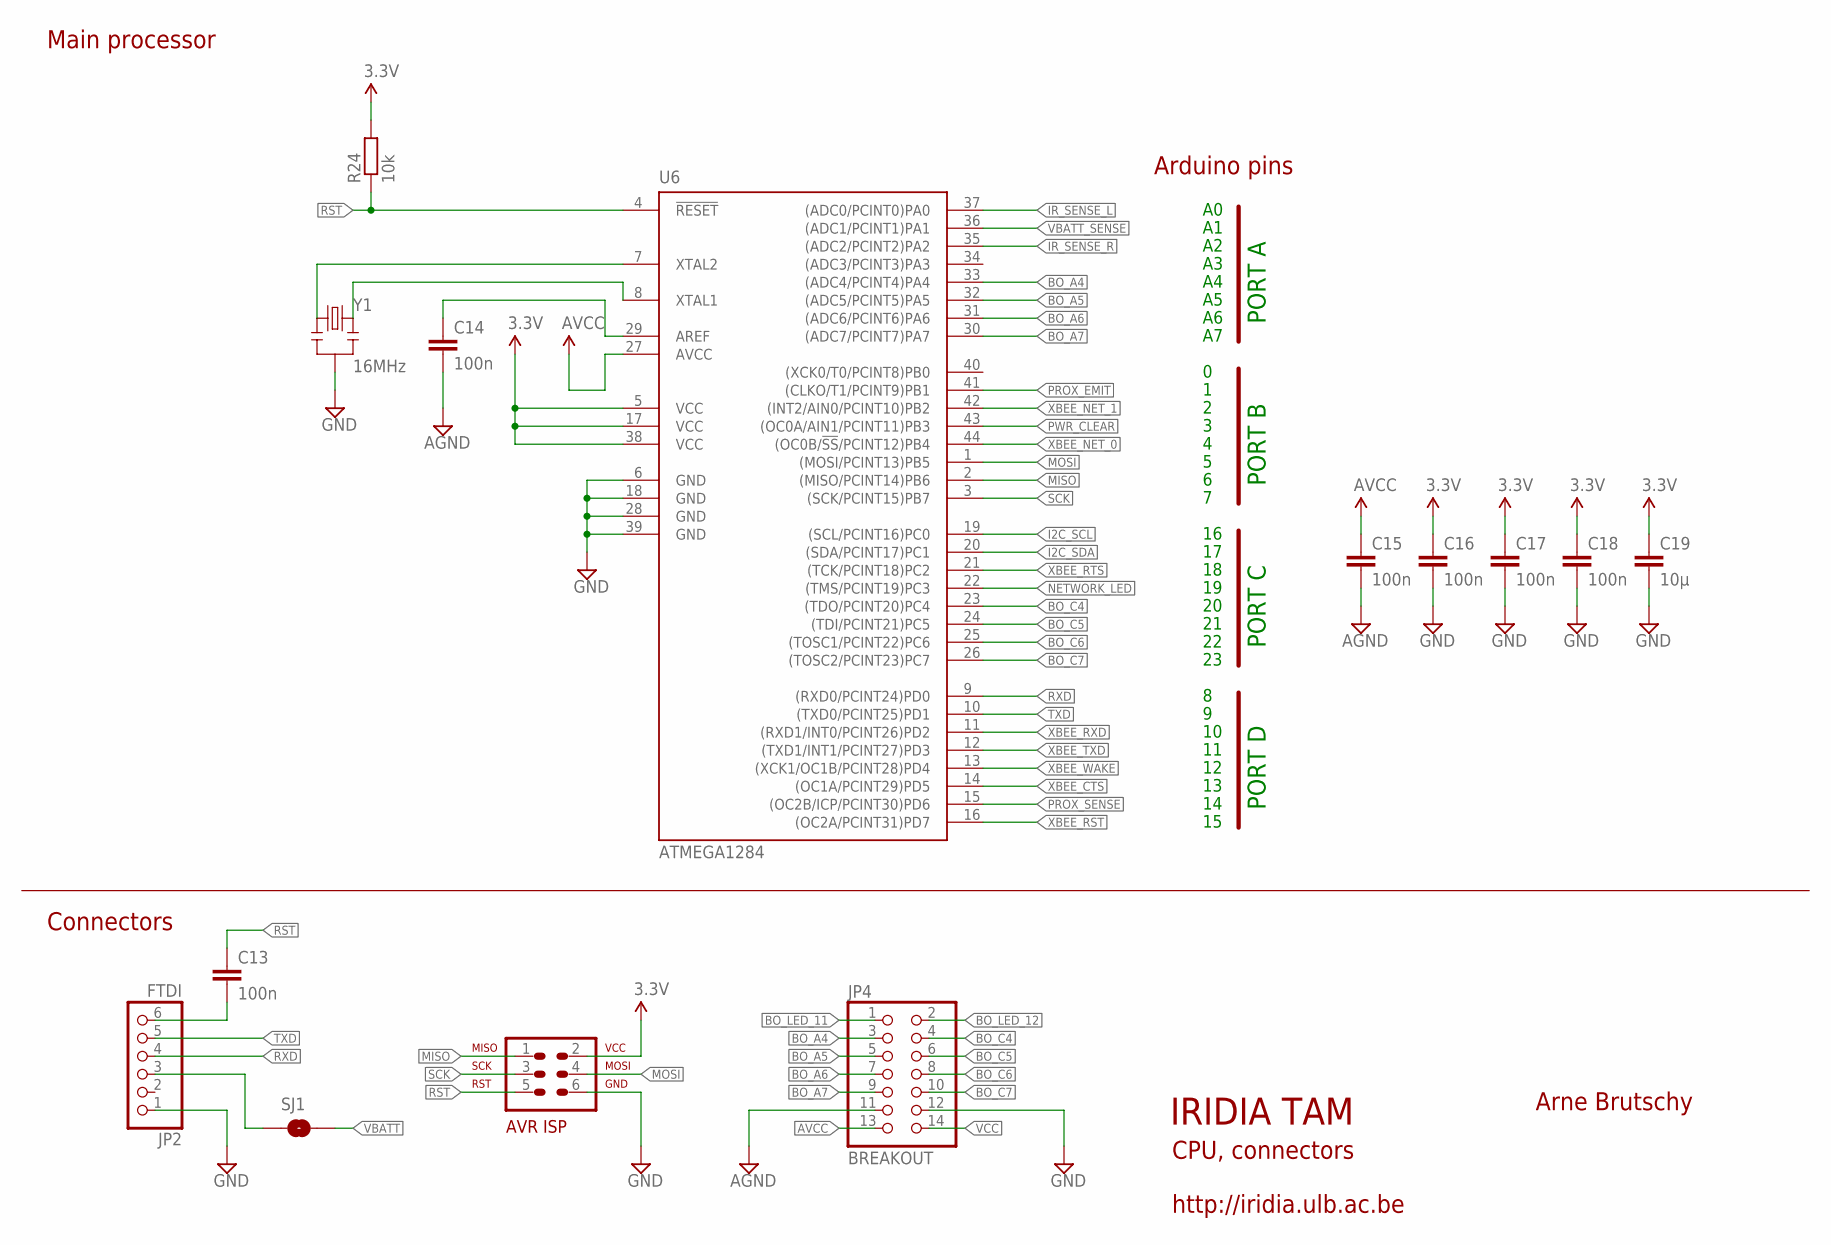
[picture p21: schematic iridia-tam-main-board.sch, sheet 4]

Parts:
C13, C14, C15, C16, C17, C18: 100n; C0603
C19: 10µ; C0805
JP2: FTDI; 1X06SMD/90
JP3: ISP; AVR-ISP-6
JP4: BREAKOUT; 2X07SMD
R24: 10k; R0603
SJ1: SOLDERJUMPERTRACE; SJ_2S-TRACE
U6: ATMEGA1284; TQFP44
Y1: 16MHz; RESONATOR-SMD

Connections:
AGND: C14.2, C15.2, JP4.11; also elsewhere on the board
AREF: C14.1, U6.29 (AREF)
AVCC: C15.1, JP4.13, U6.27 (AVCC); also elsewhere on the board
BO_A4: JP4.3, U6.33 ((ADC4/PCINT4)PA4)
BO_A5: JP4.5, U6.32 ((ADC5/PCINT5)PA5)
BO_A6: JP4.7, U6.31 ((ADC6/PCINT6)PA6)
BO_A7: JP4.9, U6.30 ((ADC7/PCINT7)PA7)
BO_C4: JP4.4, U6.23 ((TDO/PCINT20)PC4)
BO_C5: JP4.6, U6.24 ((TDI/PCINT21)PC5)
BO_C6: JP4.8, U6.25 ((TOSC1/PCINT22)PC6)
BO_C7: JP4.10, U6.26 ((TOSC2/PCINT23)PC7)
BO_LED_11: JP4.1; also elsewhere on the board
BO_LED_12: JP4.2; also elsewhere on the board
FTDI_RST1: C13.2, JP2.6
GND: C16.2, C17.2, C18.2, C19.2, JP2.1, JP3.6, JP4.12, U6.6 (GND), U6.18 (GND), U6.28 (GND), U6.39 (GND), Y1.2; also elsewhere on the board
I2C_SCL: U6.19 ((SCL/PCINT16)PC0); also elsewhere on the board
I2C_SDA: U6.20 ((SDA/PCINT17)PC1); also elsewhere on the board
IR_SENSE_L: U6.37 ((ADC0/PCINT0)PA0); also elsewhere on the board
IR_SENSE_R: U6.35 ((ADC2/PCINT2)PA2); also elsewhere on the board
MISO: JP3.1, U6.2 ((MISO/PCINT14)PB6)
MOSI: JP3.4, U6.1 ((MOSI/PCINT13)PB5)
unnamed: JP2.3, SJ1.1
NETWORK_LED: U6.22 ((TMS/PCINT19)PC3); also elsewhere on the board
PROX_EMIT: U6.41 ((CLKO/T1/PCINT9)PB1); also elsewhere on the board
PROX_SENSE: U6.15 ((OC2B/ICP/PCINT30)PD6); also elsewhere on the board
PWR_CLEAR: U6.43 ((OC0A/AIN1/PCINT11)PB3); also elsewhere on the board
RST: C13.1, JP3.5, R24.1, U6.4 (!RESET); also elsewhere on the board
RXD: JP2.4, U6.9 ((RXD0/PCINT24)PD0)
SCK: JP3.3, U6.3 ((SCK/PCINT15)PB7)
TXD: JP2.5, U6.10 ((TXD0/PCINT25)PD1)
VBATT: SJ1.2; also elsewhere on the board
VBATT_SENSE: U6.36 ((ADC1/PCINT1)PA1); also elsewhere on the board
VCC: C16.1, C17.1, C18.1, C19.1, JP3.2, JP4.14, R24.2, U6.5 (VCC), U6.17 (VCC), U6.38 (VCC); also elsewhere on the board
XBEE_CTS: U6.14 ((OC1A/PCINT29)PD5); also elsewhere on the board
XBEE_NET_0: U6.44 ((OC0B/!SS!/PCINT12)PB4); also elsewhere on the board
XBEE_NET_1: U6.42 ((INT2/AIN0/PCINT10)PB2); also elsewhere on the board
XBEE_RST: U6.16 ((OC2A/PCINT31)PD7); also elsewhere on the board
XBEE_RTS: U6.21 ((TCK/PCINT18)PC2); also elsewhere on the board
XBEE_RXD: U6.11 ((RXD1/INT0/PCINT26)PD2); also elsewhere on the board
XBEE_TXD: U6.12 ((TXD1/INT1/PCINT27)PD3); also elsewhere on the board
XBEE_WAKE: U6.13 ((XCK1/OC1B/PCINT28)PD4); also elsewhere on the board
Y1_1: U6.7 (XTAL2), Y1.1
Y1_2: U6.8 (XTAL1), Y1.3

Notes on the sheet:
IRIDIA TAM
Arne Brutschy
http://iridia.ulb.ac.be
CPU, connectors
Main processor
Connectors
Arduino pins
PORT A
PORT B
PORT C
PORT D

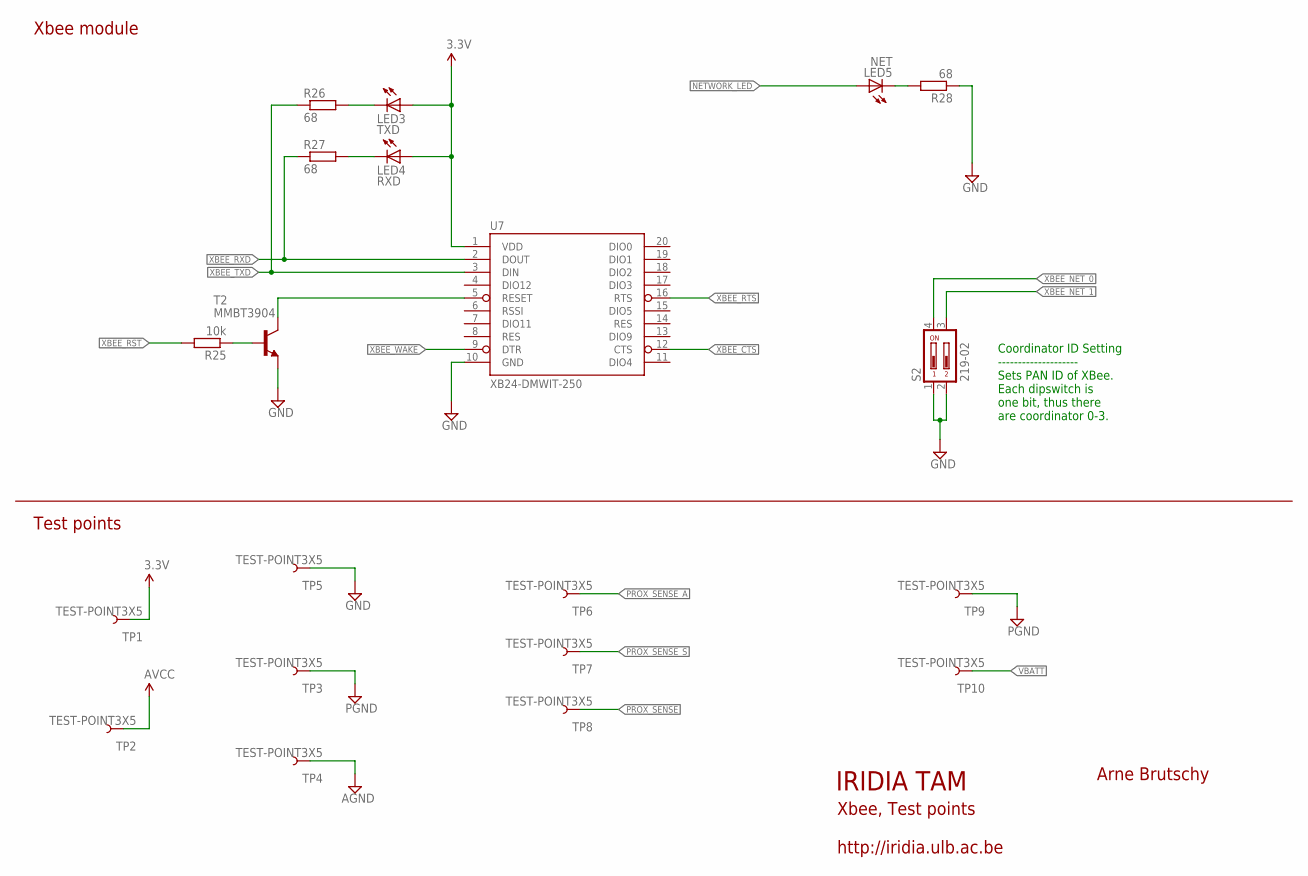
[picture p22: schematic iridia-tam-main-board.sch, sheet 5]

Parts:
LED3: TXD; CHIPLED_0805
LED4: RXD; CHIPLED_0805
LED5: NET; CHIPLED_0805
R25: 10k; R0603
R26, R27, R28: 68; R0603
S2: 219-02; CTS-219-02
T2: MMBT3904; SOT23-BEC
TP1, TP2, TP3, TP4, TP5, TP6, TP7, TP8, TP9, TP10: TEST-POINT3X5; PAD.03X.05
U7: XB24-DMWIT-250; XBEE-SMD

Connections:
AGND: TP4.P$1; also elsewhere on the board
AVCC: TP2.P$1; also elsewhere on the board
GND: R28.1, S2.1, S2.2, T2.E, TP5.P$1, U7.10 (GND); also elsewhere on the board
unnamed: LED4.C, R27.2
unnamed: R25.1, T2.B
unnamed: LED3.C, R26.2
unnamed: T2.C, U7.5 (RESET)
unnamed: LED5.C, R28.2
NETWORK_LED: LED5.A; also elsewhere on the board
PGND: TP3.P$1, TP9.P$1; also elsewhere on the board
PROX_SENSE: TP8.P$1; also elsewhere on the board
PROX_SENSE_A: TP6.P$1; also elsewhere on the board
PROX_SENSE_S: TP7.P$1; also elsewhere on the board
VBATT: TP10.P$1; also elsewhere on the board
VCC: LED3.A, LED4.A, TP1.P$1, U7.1 (VDD); also elsewhere on the board
XBEE_CTS: U7.12 (CTS); also elsewhere on the board
XBEE_NET_0: S2.4; also elsewhere on the board
XBEE_NET_1: S2.3; also elsewhere on the board
XBEE_RST: R25.2; also elsewhere on the board
XBEE_RTS: U7.16 (RTS); also elsewhere on the board
XBEE_RXD: R27.1, U7.2 (DOUT); also elsewhere on the board
XBEE_TXD: R26.1, U7.3 (DIN); also elsewhere on the board
XBEE_WAKE: U7.9 (DTR); also elsewhere on the board

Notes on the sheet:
Xbee module
IRIDIA TAM
Arne Brutschy
http://iridia.ulb.ac.be
Xbee, Test points
Test points
Coordinator ID Setting -------------------- Sets PAN ID of XBee. Each dipswitch is one bit, thus there are coordinator 0-3.

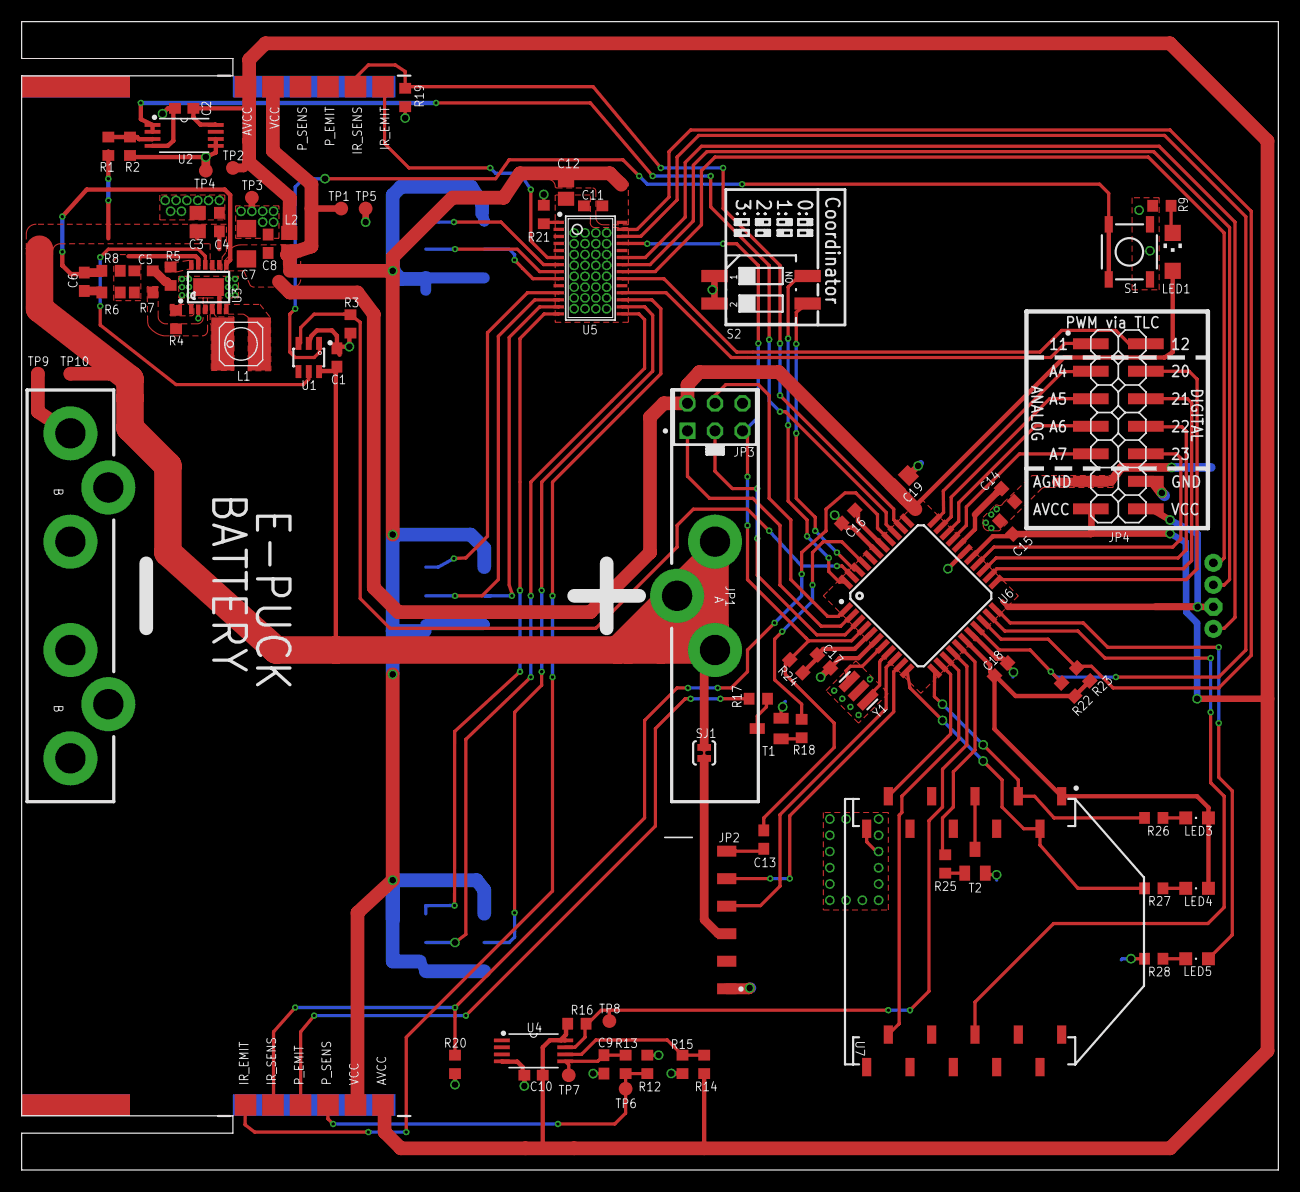
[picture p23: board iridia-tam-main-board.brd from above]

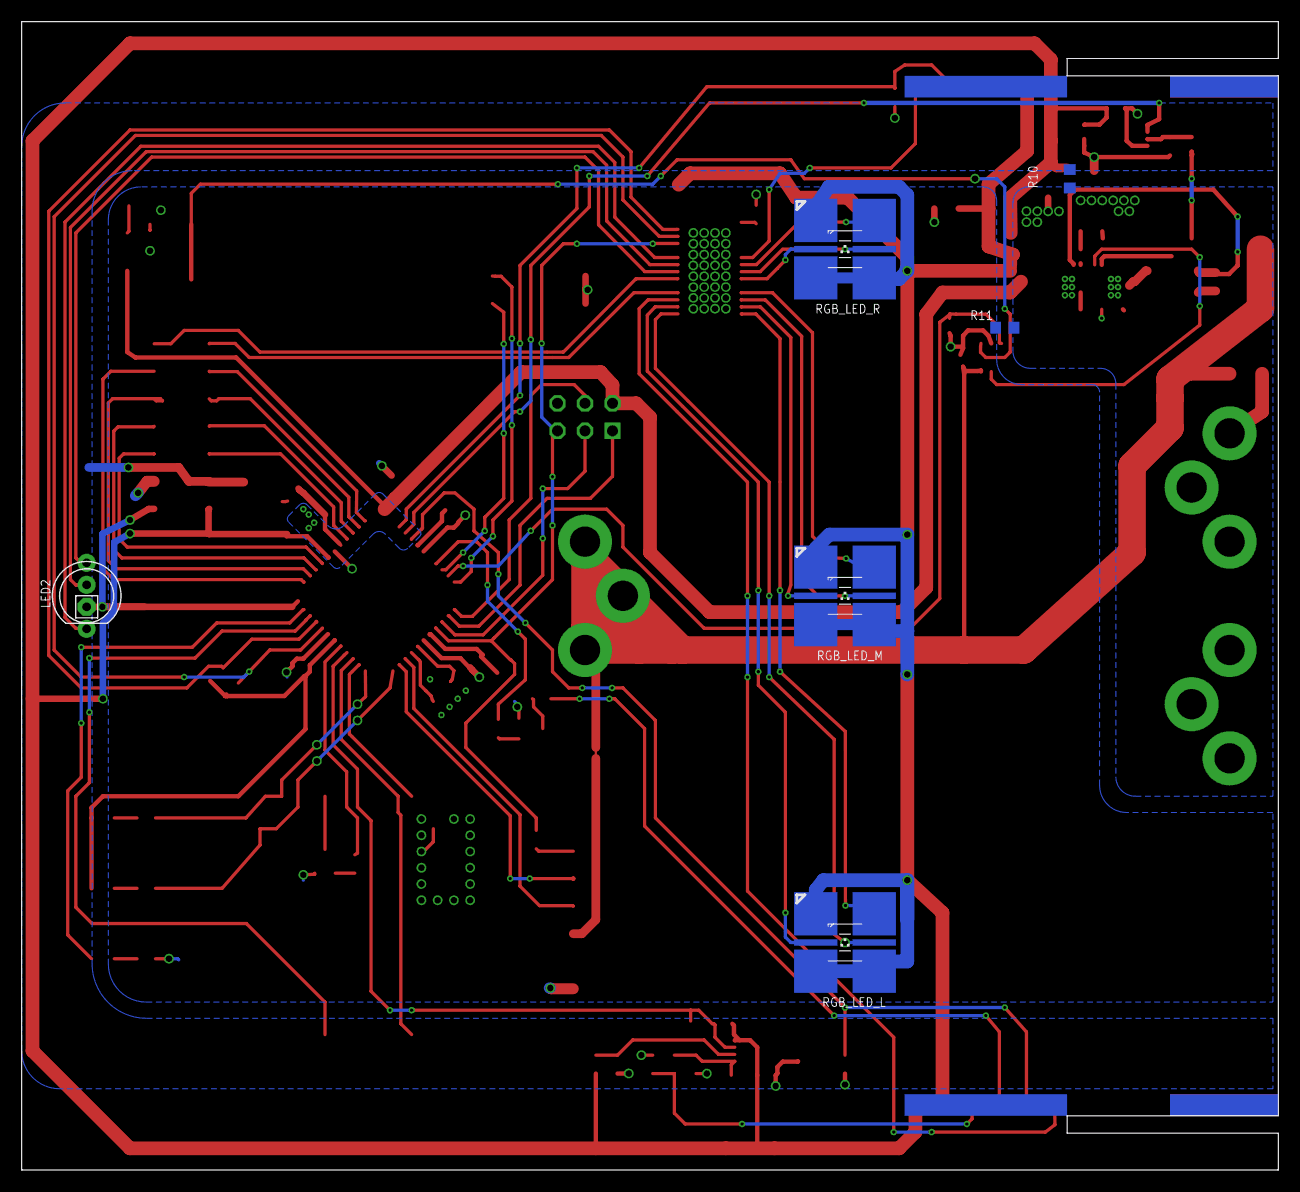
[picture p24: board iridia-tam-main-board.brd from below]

Board: 2 copper layers, 116.0 x 106.0 mm, 86 parts (6 on the bottom side), 81 nets.

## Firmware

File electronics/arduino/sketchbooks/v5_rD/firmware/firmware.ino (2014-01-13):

//IRcom library
#include <ircom.h>
#include <ircomReceive.h>
#include <ircomMessages.h>
#include <ircomTools.h>
#include <ircomSend.h>

// all libs below are included in the TAM git
#include <I2C.h>
#include <TLC59116.h>        // based on http://brmlab.cz/project/ledbar
#include <XBee.h>            // based on http://code.google.com/p/xbee-arduino/ (v0.4b)


/********************************************************************
 *
 * Example Arduino Controller for the IRIDIA TAM
 *
 ********************************************************************/

#define TAM_FIRMWARE_VERSION  "v5rD-0.2"

/**
 * Debug macros which enable bits of code used for debugging the firmware.
 */
#define DEBUG_ENABLE_SERIAL_OUTPUT    // disabled all serial printout and strings

#define ENABLE_IRCOM

#define DEBUG_TAM_INFO
#define DEBUG_XBEE_INFO


/**
 * Controls which messages are logged.
 */
// general output classes
#define P_INFO(format, ...) p( "[INFO] %04d " format, cycle, ## __VA_ARGS__ )
//#define P_INFO(format, ...)
#define P_WARN(format, ...) p( "[WARN] %04d " format, cycle, ## __VA_ARGS__ )
//#define P_INFO(format, ...)

// xbee-related output
#define P_XBEE(format, ...) p( "[XBEE] " format, ## __VA_ARGS__ )
//#define P_XBEE(format, ...)
//#define P_XBEE_RECV(format, ...) p( "[XBRX] %04d " format, cycle, ## __VA_ARGS__ )
#define P_XBEE_RECV(format, ...)
#define P_XBEE_SEND(format, ...) p( "[XBTX] %04d " format, cycle, ## __VA_ARGS__ )
//#define P_XBEE_SEND(format, ...)
//#define P_XBEE_AT(format, ...) p( "[XBAT] %04d " format, cycle, ## __VA_ARGS__ )
#define P_XBEE_AT(format, ...)

// light barrier output/debug
#define P_LIBA(format, ...) p( "[LIBA] %04d " format, cycle, ## __VA_ARGS__ )
//#define P_LIBA(format, ...)

// proximity sensor output/debug
//#define P_PROX(format, ...) p( "[PROX] %04d " format, cycle, ## __VA_ARGS__ )
#define P_PROX(format, ...)

// ircom output/debug
#define P_IRCOM(format, ...) p( "[IRCOM] %04d " format, cycle, ## __VA_ARGS__ )
//#define P_IRCOM(format, ...)


/**
 * Definition of packet types used in Xbee communication.
 * Packet type MUST be designated in first byte.
 */
// TAM to coordinator
#define PACKET_TYPE_TC_CURRENT_STATE      0  // state report
#define PACKET_TYPE_TC_READ_ROBOT_RESULT  1  // result of read robot operation
#define PACKET_TYPE_TC_WRITE_ROBOT_RESULT 2  // result of write robot operation
// coordinator to TAM
#define PACKET_TYPE_CT_SET_LEDS          10
#define PACKET_TYPE_CT_READ_ROBOT        11
#define PACKET_TYPE_CT_WRITE_ROBOT       12
#define PACKET_TYPE_CT_SHUTDOWN          13


/**
 * Definition of constants (thresholds, intervals and times). 
 * Adjust only if you know what you are doing, ESPECIALLY the network stuff!
 */
// delay between switching the light barrier on and off
#define IR_WAIT_TIME     2
// threshold required between IR LED on and off in the reading of the IR transistor
#define IR_THRESHOLD   120


// threshold for low battery voltage detection
#define BATT_VOLTAGE_WARN     3000
// threshold for low battery voltage detection
#define BATT_VOLTAGE_SHUTDOWN 2700
// number of cycles the battery has to be below BATT_VOLTAGE_SHUTDOWN before we shut down
// used to filter battery voltage sensing
#define BATT_UNDER_VOLTAGE_COUNTER_THRESHOLD 10


// if defined, the TAM tries to resolve the coordinator via network on boot
// if undefined, uses hard-coded coordinator address defined below
#define RESOLVE_COORDINATOR
// maximum number of resolve commands, if it fails it uses the hard-coded
// coordinator address defined below
#define RESOLVE_COORDINATOR_MAX_TRIES 500


// minimum length of main control cycle in ms
// cycle might be slightly longer due to fuction calls
#define CYCLE_LENGTH 10
// interval at which we send our status to the coordinator, expressed in milliseconds
#define HEARTBEAT_INTERVAL 10000
// timeout for waiting for responses for the packets sent by us, expressed in milliseconds
#define RESPONSE_TIMEOUT 1000

// interval at which we send the ircom data while the robot is inside the TAM, expressed in ms
#define IRCOM_SEND_INTERVAL 200


/**
 * Definition of hardware pins. Do NOT change this.
 */
#define XBEE_WAKE_PIN     12  // xbee sleep control
#define XBEE_CTS_PIN      13  // xbee serial cts (unused at the moment, use for large data)
#define XBEE_RTS_PIN      18  // xbee serial rts (unused at the moment, use for large data)
#define XBEE_RST_PIN      15  // xbee reset

#define XBEE_NET_ID_0_PIN  2  // bit 0 of xbee PAN id
#define XBEE_NET_ID_1_PIN  4  // bit 1 of xbee PAN id

#define NETWORK_LED_PIN   19

#define POWER_OFF_PIN      3  // all-mighty power-off pin for PSU
#define VBATT_SENSE_PIN   A1  // signal VBATT_SENSE

#define PROX_SENSE_PIN    14  // ICP pin fixed to internal Timer
#define PROX_EMIT_PIN      1

#define IRB_SENSE_PIN     A2  // signal IR_SENSE_L
#define IRF_SENSE_PIN     A0  // signal IR_SENSE_R


// pin definitions of the LEDs connected to the TLC
enum TlcLedPins {
  LED_IR_R,
  LED_RED_R,
  LED_BLUE_R,   // right side leds (IR + RGB)
  LED_GREEN_R,
  LED_RED_M,
  LED_BLUE_M,
  LED_GREEN_M,  // middle led (RGB)
  LED_RED_L,
  LED_BLUE_L,   // left side leds (IR + RGB)
  LED_GREEN_L,
  LED_IR_L,
  LED_BO,       // unused (breakout 0)
  LED_B1,       // unused (breakout 1)
  LED_BLUE_T,
  LED_GREEN_T,
  LED_RED_T     // top led (RGB)
};

// adapt this however your board is populated
const uint8_t NUM_LEDS = 4;
const uint8_t LEDS_RED[NUM_LEDS] = {
  LED_RED_R,
  LED_RED_M,
  LED_RED_L,
  LED_RED_T
};
const uint8_t LEDS_GREEN[NUM_LEDS] = {
  LED_GREEN_R,
  LED_GREEN_M,
  LED_GREEN_L,
  LED_GREEN_T
};
const uint8_t LEDS_BLUE[NUM_LEDS] = {
  LED_BLUE_R,
  LED_BLUE_M,
  LED_BLUE_L,
  LED_BLUE_T
};

// type definition for the state of the TAM
typedef struct {
  uint8_t redLed;
  uint8_t greenLed;
  uint8_t blueLed;
  boolean robotPresent;
  uint8_t robotData;
} state_t;


/**
 * Global variables
 */

// current state (RGB LED value and robot presence)
state_t currentState;
// state as reported last to coordinator via Xbee
state_t lastReportedState;
// if true, the TAM reports the state to the coordinator in the next cycle
boolean reportState = false;

//
// main objects initialization
// if you don't to this here the bloody TAM resets
//
TLC59116 tlc = TLC59116();  // TLC that controls the PWM leds
XBee xbee = XBee();         // Xbee library

// Variables for reading light barriers analog
int irReadPreF;
int irReadPreB;
// stages of checking light barriers
byte irStage = 0;
// this can be considered as 8 booleans, used to filter the IR light barrier reading
uint8_t irBoolsF = 0;
uint8_t irBoolsB = 0;
uint8_t irBit = 1;

// voltage check variables
int battVoltage = 0;
uint8_t battUnderVoltageCounter = 0;

// Xbee variables
uint32_t xbeeCoordinatorAddressHigh;    // 64bit coordinator address, HSBs
uint32_t xbeeCoordinatorAddressLow;     // 64bit coordinator address, LSBs
// fallback coordinator address, MSB and LSB
const uint32_t xbeeHardcodedCoordinatorAddressesHigh = 0x0013A200;
const uint32_t xbeeHardcodedCoordinatorAddressesLow[4] = { 0x408C04A4, 0x408C04C5, 0x408D6EB4, 0x408D6EA2 };
XBeeAddress64 coordAddr64;              // struct for address
DMTxRequest statePacket;                // packet for sending TAM state
DMTxStatusResponse statePacketResponse; // response for sending TAM state packet
uint16_t nodeDiscoveryTimeout;

// variables used for AT requests (management commands for Xbee)
uint8_t atCmd[2];
AtCommandRequest atRequest;
AtCommandResponse atResponse;

// count of control cycles, each cycle = 0.1 secs
int cycle = 0;

// set to true if the last packet sent is still awaiting response
// used for getting packet ACKs asynchronously
boolean lastPacketAwaitingResponse = false;
// frame id of the last packet sent
uint8_t lastPacketFrameId = 0;
// timestamp of the last packet sent
unsigned long lastPacketSentAt = 0;
// timestamp of last heartbeat
unsigned long lastHeartbeatSentAt = 0;

// payload of the state packet
uint8_t statePayload[8];

// IRcom variables
#ifdef ENABLE_IRCOM
int irComDataToWrite = 0;
unsigned long IrComLastSendAt = 0;
#endif

// current time
unsigned long now = 0;


/***************************************************************************************************/
/***************************************************************************************************/


/**
 * Small helper function that emulates printf().
 * Disabled by DEBUG_ENABLE_SERIAL_OUTPUT.
 * @param fmt  format string, followed by possible parameters
 */
void p(const char *fmt, ... )
{
#ifdef DEBUG_ENABLE_SERIAL_OUTPUT
  char tmp[128]; // resulting string limited to 128 chars
  va_list args;
  va_start(args, fmt );
  vsnprintf(tmp, 128, fmt, args);
  va_end (args);
  Serial.print(tmp);
#else
#endif
}


/**
 * Swaps the endianness a 16bit unsigned integer.
 * @param val  pointer to integer to swap
 */
void swapEndian16(uint16_t &val)
{
  val = (val<<8) | (val>>8);
}


/**
 * Swaps the endianness a 32bit unsigned integer.
 * @param val  pointer to integer to swap
 */
void swapEndian32(uint32_t &val)
{
  val = (val<<24) | ((val<<8) & 0x00ff0000) | ((val>>8) & 0x0000ff00) | (val>>24);
}


/**
 * Prepare serial and set necessary digital pins to output.
 * Also initializes the Xbee module and resolves the address of the coordinator.
 */
void setup()
{
  Serial.begin(57600);
  Serial.println("Starting IRIDIA TAM");
  
#ifdef DEBUG_TAM_INFO
  p("Firmware version: %s\n\r", TAM_FIRMWARE_VERSION);
#endif

  // currently unused
  pinMode(XBEE_WAKE_PIN, OUTPUT);
  digitalWrite(XBEE_WAKE_PIN, LOW);
  pinMode(XBEE_CTS_PIN, OUTPUT);
  digitalWrite(XBEE_CTS_PIN, LOW);
  pinMode(XBEE_RTS_PIN, OUTPUT);
  digitalWrite(XBEE_RTS_PIN, LOW);
  
  // sensing for front and back IR barrier
  pinMode(IRF_SENSE_PIN, INPUT);
  pinMode(IRB_SENSE_PIN, INPUT);
  
  // setup psu pins  
  pinMode(VBATT_SENSE_PIN, INPUT);
  pinMode(POWER_OFF_PIN, OUTPUT);
  digitalWrite(POWER_OFF_PIN, LOW);

  // emit and sensing for proximity sensor
  pinMode(PROX_EMIT_PIN, OUTPUT);
  digitalWrite(PROX_EMIT_PIN, LOW);
  pinMode(PROX_SENSE_PIN, INPUT);
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

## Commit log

2013-04-03 Added coordinator, eagle files, 3d model files, and photos
    [TAM-diffuser.skp, TAM-left-board-ver4-revB.skp, TAM-main-board-ver4-revB.skp, TAM-right-board-ver4-revB.skp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]
2013-04-03 Removed outdated gerbers
    [iridia-tam-left-board.GBL, iridia-tam-left-board.GBO, iridia-tam-left-board.GBS, iridia-tam-left-board.GTL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]
2014-01-13 Updated to final version 5 revision D
    [TAM-assembly-ver5-revA.skp, TAM-left-board-ver4-revB.skp, TAM-main-board-ver4-revB.skp, TAM-right-board-ver4-revB.skp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]
2014-01-14 Updated BOMs
    [iridia-tam-left-board.xls, iridia-tam-main-board.xls, iridia-tam-right-board.xls]
2014-08-28 Minor fixes in bom
    [iridia-tam-right-board.xls]
